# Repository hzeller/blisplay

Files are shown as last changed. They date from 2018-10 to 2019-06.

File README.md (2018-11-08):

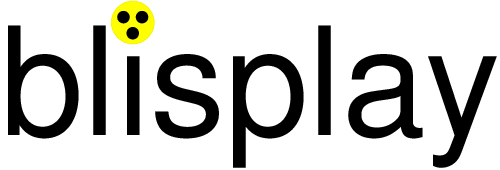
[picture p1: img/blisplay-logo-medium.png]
Blisplay logo


<h1 align="center">an Open Source Hardware tactile display for the blind.</h1>

## Seeing for the blind: make it tactile
Without optical sense there is another way of conveying spatial information
in an accessible way by providing a [tactile experience][tactile-graphic].
Usually, these are 'offline' methods by using swell papers or embossers to
generate a surface representing graphics.

I wanted to make a "display" that can provide such tactile surface directly from
the computer. Of course, it would be a huge effort (and pretty heavy) to build
a surface with tens of thousands of actuators to poke out little dots, so
instead let's just strap a small amount of actuated dots just covering the
fingertip under the finger and actuate them depending on where the finger is
in the image. A display for the blind, let's call it **blisplay**.

#### About this README

I have to apologize to visually impaired readers of this README as it
contains are a couple of pictures in here which make it less accessible.
But these hopefully help your sighted peers to get them started
building the device. To make up for it, there are some explanations that
might sound lengthy and detailed to sighted readers - these are part of the
proverbial thousand words describing the pictures.

#### Direct optical to tactile

There is a simple direct way to do it: mount a camera under the set of tactile
pixels, watching the optical image underneath, directly translating optical
to tactile information; while moving the finger over the surface, the image
underneath will be translated to tactile information, allowing the user to
experience the full image by following the lines on the surface. This is the
first implementation as it is straightforward.

So the first prototype is sitting on a stand-off to be able to watch the
surface underneath.

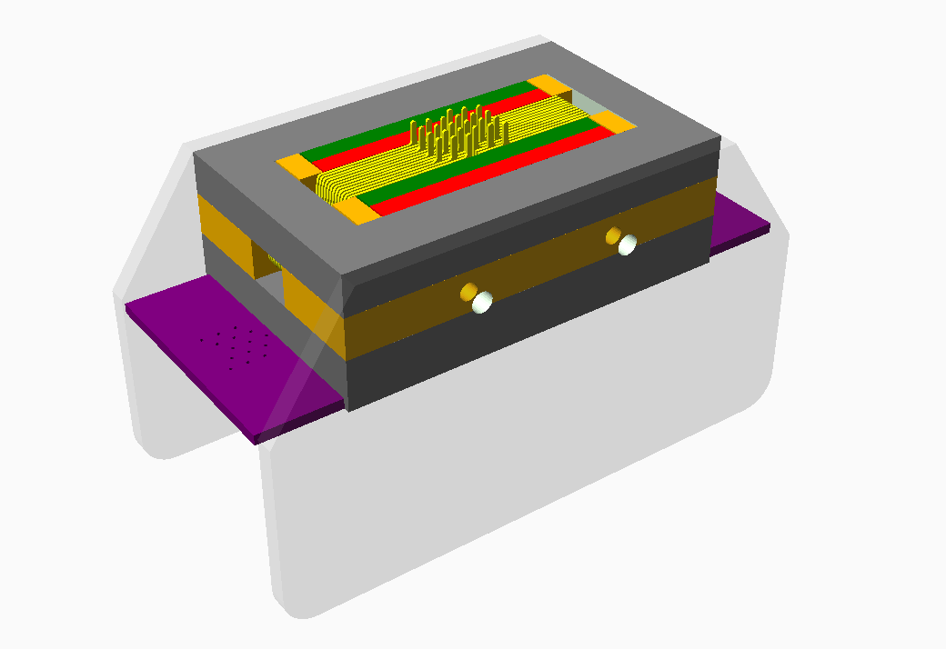
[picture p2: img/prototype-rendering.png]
Rendering of a fully assembled unit
  |
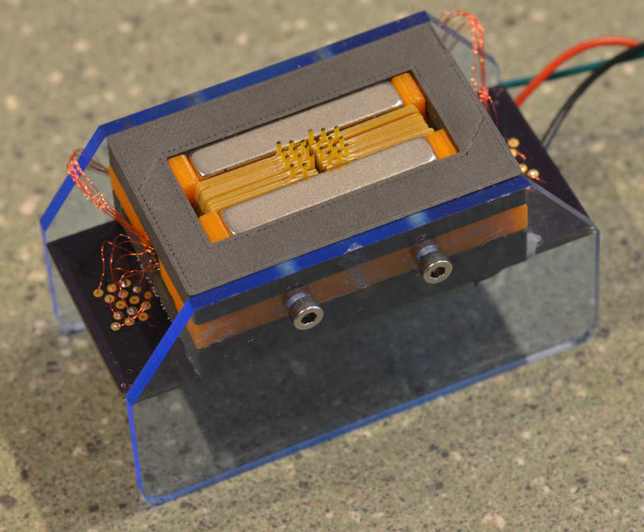
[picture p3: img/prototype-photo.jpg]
Photo of prototype unit
   
-----------------------------------|-------------------------|
Blisplay assembly rendering        | Photo of the actual unit|

#### Display an image from a computer

Another way is to show a picture directly from a computer by having it watch
the position of the finger and present the pixels representing the current
covered area. There are various ways doing it, e.g. with a graphic tablet
encoding the absolute position. Or, these days, it should be easy with the
ubiquitous smart-phones: load an image on the phone and point its camera to
the surface the hand is moving over; with simple image processing, we can
follow the finger relative to the background and send the right tactile
pattern to the device.

### Design goal
The design goal of this project is to make it simple to build
by some technically inclined person for their blind peers.

Right now, I am working on hashing out the most practical way to do so. The
first prototype is already pretty simple, but some more simplification
needs to be done (in particular for the coil wiring, see below).

I would hope for build parties in the future in which hacker-spaces
build devices for their local blind community and improve on the design based
on the feedback.

### Status
The first prototype is assembled and shows desirable functionality and force
of the actuators. The ADNS-3050 chip used as camera is connected but has yet
to be debugged to get some reading of the frame; also the lens-assembly for
getting an image on the sensor has to be worked on.

The current device is a little bit bulky (about 45mmx90mm), but ideas lined-up
for a second prototype will reduce that. Current resolution is about 2mm in a
4x6 grid (8mm x 12mm). This is already pretty close to the spacial resolution of
finger-tips, but future iterations will hopefully improve that more.

### History
What motivated all this ? I have a blind friend for whom I made tactile maps
by gluing thread on paper or transferring graphics using swell-paper
as well as other means to make graphical things accessible.
But in particular I wanted to directly provide images from a computer without
these detours.

In about 2006, I made the very first prototype of this project of a location
aware pixel actuator, [using a modified relay solenoid strapped to a pen of a
graphics tablet](./img/old-prototype-2006.jpg). The single pixels was not very
intuitive though as it requires a lot of scanning by finger. Fast forward do
2018, time to revisit this project and use 3D printing and hobbyist-affordable
PCB making that came up in the meantime to make this much more useful.

## Actuators

There are several ways we could think of actuating raising dots to get the
tactile experience. One of the most important constraints though will be size:
we need to have these pixels reasonably dense and a few of them to be able
to be useful. In the first prototype, these are 4x6 pixels in a 2mm grid
(somewhat diagonal grid as we see later). Also, ideally we can modulate the
force of the pixels to emulate different elevations.

The modulation constraint means that we can't use a bi-stable solenoid but
need to go with a moving coil or moving magnet approach.

The density constraint means that we need to optimize the use of the available
volume for the moving parts and keep supporting structure (magnets, wiring, ...)
out of the way.

### Moving coil
So let's just do the first and simplest thing that comes to mind: use a
conductor in a magnetic field, generating a [Lorentz force].
The conductor is made out of a PCB coil, essentially a square area with a
protruding bit on one side (the tactile dot) and a fulcrum in the
center other side.

#### Stack of flat coils in magnetic field
To visualize (sighted readers also see this in the images): Let's imagine
your left hand facing you with the thumb up.
The hand represents the flat coil with a conductor going across the index
finger towards your wrist, then down, and out again towards the pinkie.

The thumb is extended out and represents the little dot that will poke.
This coil/hand is hinged at the tip of the middle finger.
The magnetic field is going through the flat hand coming from the back of
your hand at the top and at the bottom into your hand pointing towards the back.

With a current through the conductor, the top conductor will move up and so will
the reversed bottom conductor through the reversed magnetic field. This coil
will hinge and move the thumb up and down.

With a stack of these coils, we can have a lot of actuators in a pretty dense
space. A stack of 12 coils are grouped in four stacks of three.
In each triplet, the first coil has the protruding dot the furthest away from
the fulcrum, the next 2mm in (as if the thumb was mounted more towards your
index finger), the next 4mm in.
That way, we can have three independently controlled pixels in that direction.
The coils are made of 0.4mm thick PCB, so the stack can be made 2mm thick with
some wiggle room to spare.
With four of these triplets, we have 4x3 pixels with a 2 mm distance between
adjacent pixels (but slightly diagonal due to the stacking).

In the following demonstration, the current direction is
shown in the traditional plus to minus direction to align with the common
Lorentz right-hand rule.

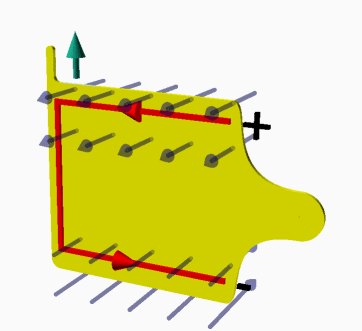
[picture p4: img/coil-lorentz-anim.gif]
Animation of forces in magnetic field
   |
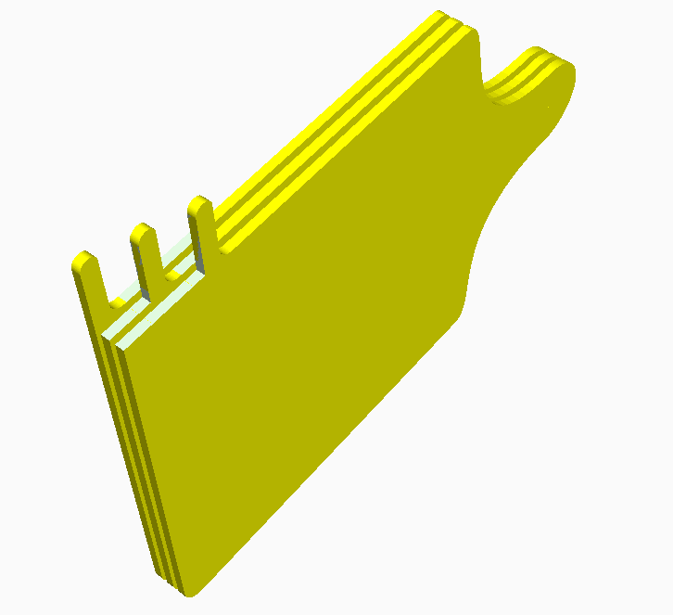
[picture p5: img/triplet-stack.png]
A stack of three coils with offset fingers
 |
-----------------------------------------------|---------------------|
Moving coil in magnetic field. Red arrow: varying current; Blue: static magnetic field; Green: resulting force | A triplet of coils with offset dots, stacked.

If we hinge two stacks right and left with the poky bits meeting at the center
we have a 6x4 pixel arrangement.

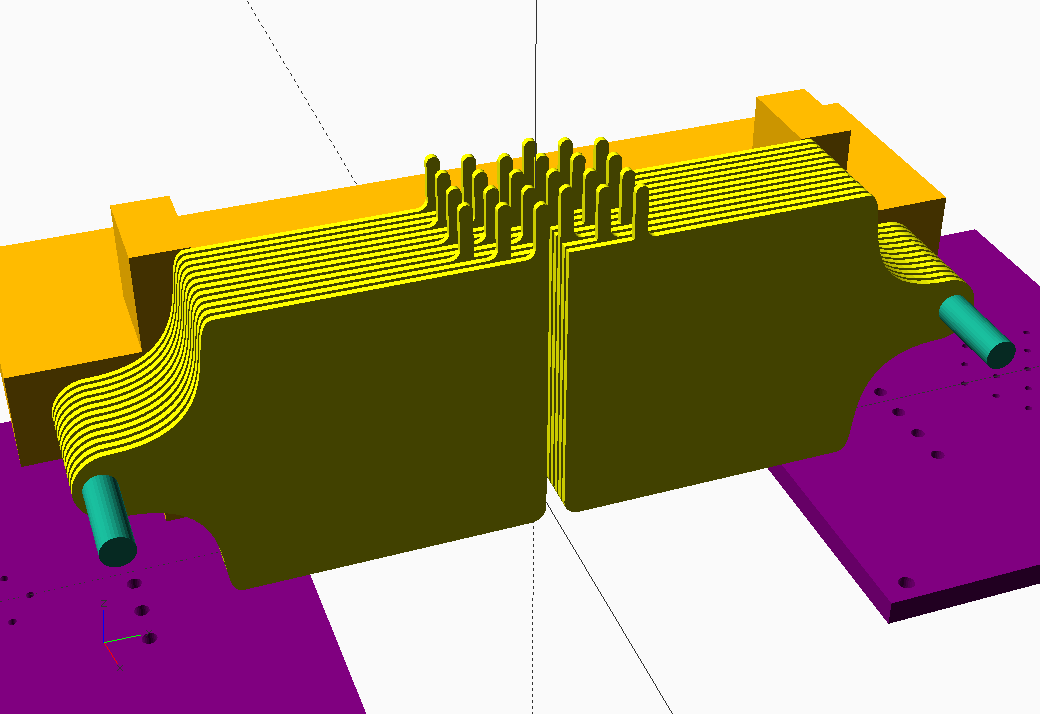
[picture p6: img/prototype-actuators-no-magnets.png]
Rendering showing view of actuators without magnets
 |
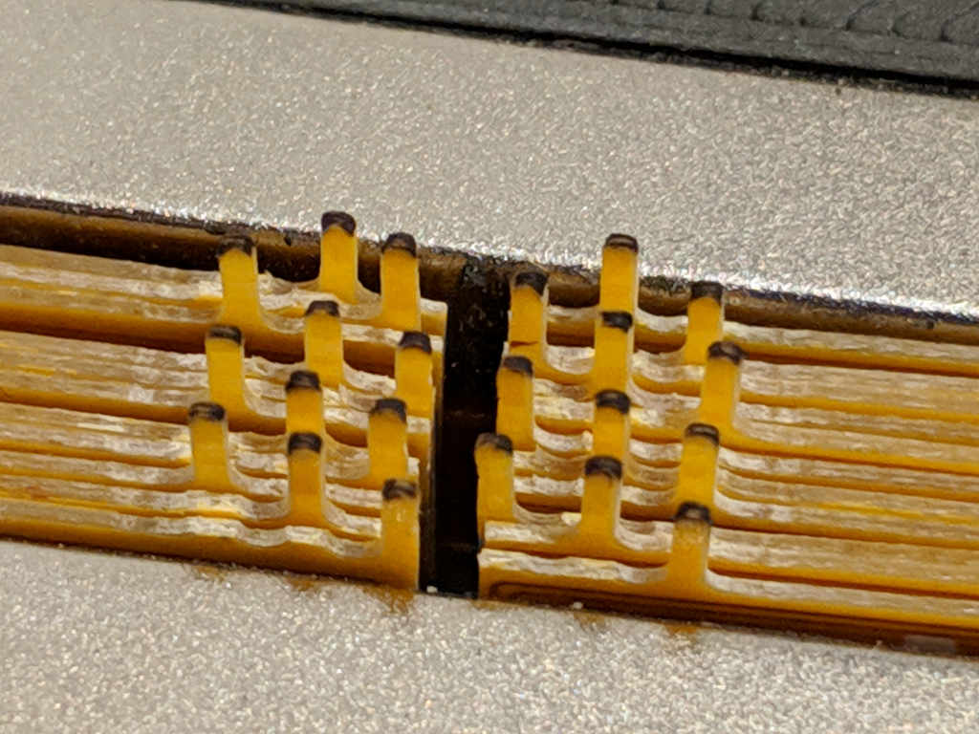
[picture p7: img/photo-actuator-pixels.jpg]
Closeup of pixels in prototype
  
-----------------------------------------------|---------------------|
View of all actuator blade coils. Hinged at opposite ends of the assembly, they allow 6x4 pixels in the center.  | Closeup of pixels in prototype (here, only 22 pixels)

With each blade coil mounted, they can be individually controlled.

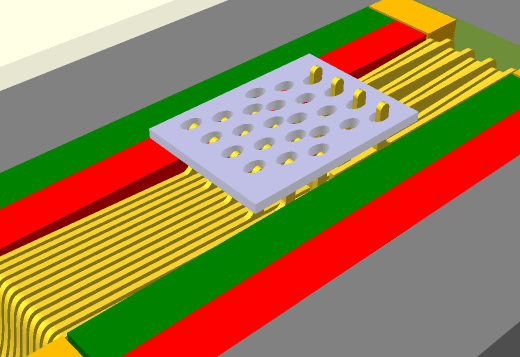
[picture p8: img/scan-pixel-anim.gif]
Animation of pixels scanning and poking through finger-pad


## Driving Circuit

The coils need to be driven in the low hundreds of milliampere; for this simple
transistor drivers are used (maybe in the future half-bridges ?).

The driving circuit for the coils are currently two identical boards with
a shift register and ULN2803 open collector driver chips. The two chained
boards are presenting itself as a 32 bit shift register to the microcontroller
and has two LEDs and allow to connect up to 30 coils. The
latch input is latching on the positive edge, so it can be used as an SPI
client.

The component choice was based on what I had lying around at home, but a
future iteration of this board will be more compact, e.g. by using
NCV7751 chips that contain 12 drivers and an SPI interface in one package
(or maybe TLE94112 with half-bridges).

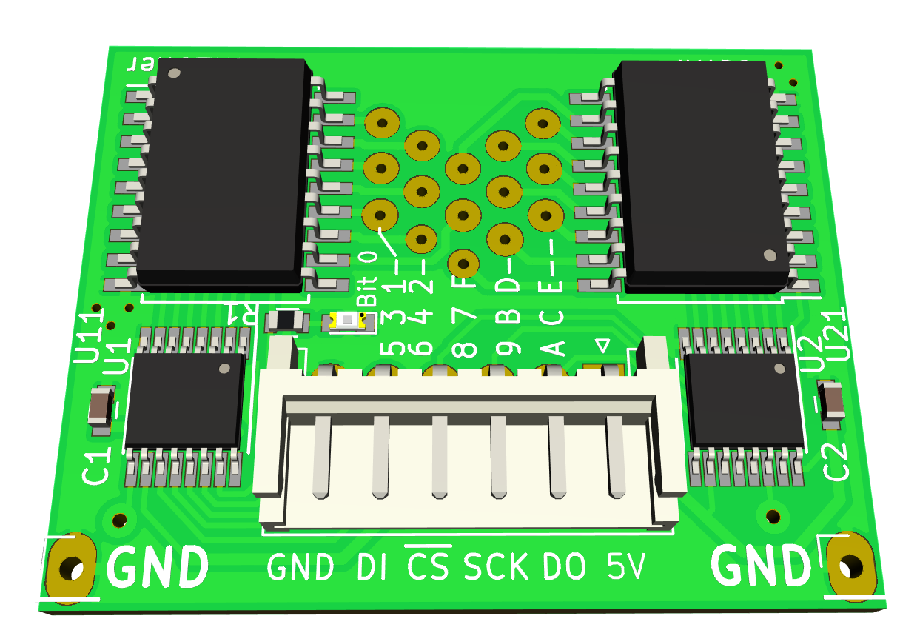
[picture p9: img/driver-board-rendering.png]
Rendering of coil-driver board
 |
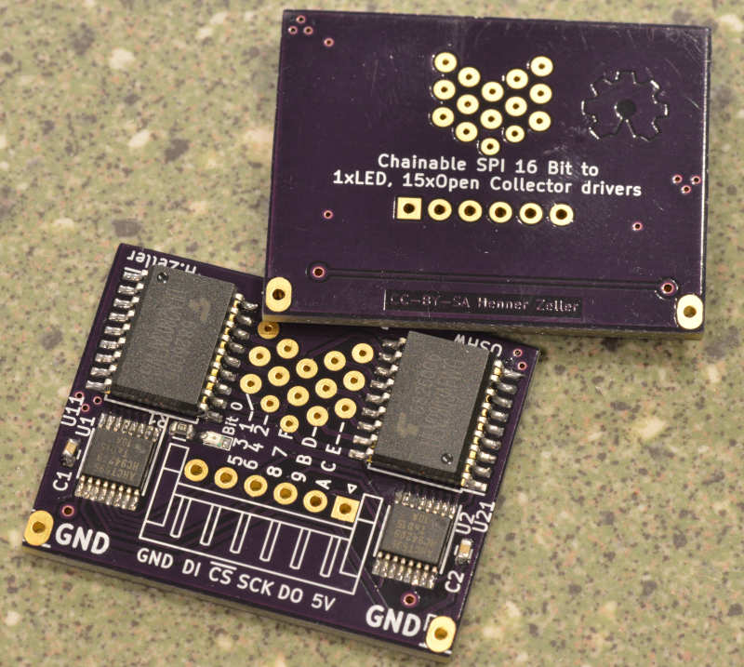
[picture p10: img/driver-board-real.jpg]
Image of soldered coil-driver board
    
--------------------------------------|-----------------------------------|
15 Transistor serial driver board     |  ... for realz                    |

## Controlling Circuit
The controlling circuit right now is a simple ATTINY85 using SPI to
communicate with the driver circuit and the ADNS-3050. Two pins are used as
Chip Select for either the camera or the coil drivers.

This prototype is mounted on a raster board. The camera does not yet
have an optical lens assembly as the readout still needs to be debugged.

A future version will likely use a Microcontroller with more pins (ATTINY44) to
be able to also drive an additional 0.96" OLED display to help visualize while
debugging.

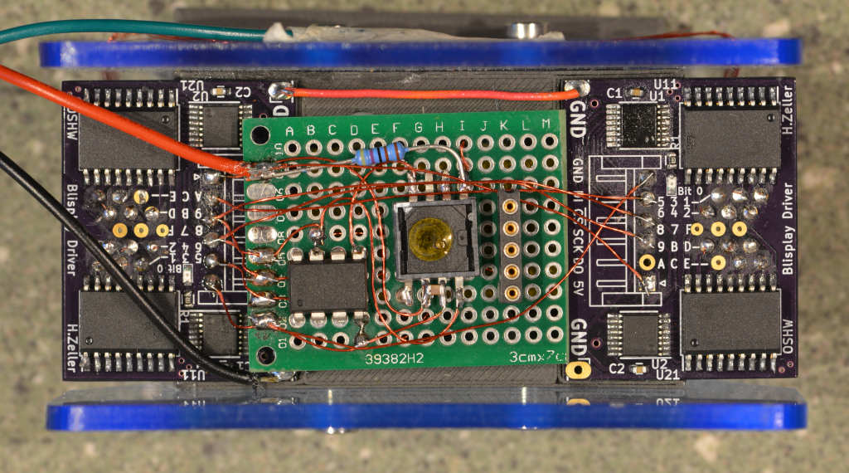
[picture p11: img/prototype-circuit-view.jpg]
Circuit from the bottom of the assembly


# Building

Right now, the prototype design is still somewhat in flux, but you can already
build a prototype. Mail me directly if you have specific questions while doing
so.

### 3D printing and laser cutting

You need to have OpenSCAD installed, then, in the top-level directory, type

```
 make
```

This will generate the following files inside a `fab/` directory:

  * `print_yokes_magnetic_filament.stl` yokes to be printed with magnetic
    filament (I found that magnetic filament is actually not that good. I ended
    up printing them hollow and fill with iron powder. The next prototype will
    just use simple iron parts from the hardware store).
  * `print_yoke_spacers.stl` The spacers, to be printed with regular,
    non-magnetic filament.
  * `lasercut_sidewall.dxf` the side-wall to elevate the assembly to have a
    free view below. These dimensions are super rough right now and will change
    once there is a lens-assembly on the camera.
  * `finger_cradle.stl` is a hollow shape keeping the finger in place over
    the actuators. You might need to adapt parameters to your finger-diameter.
    (currently does not lock into the rest of the assembly, you might need
    some double-sided tape).
  * The `assembly_tool_spacer_holder.stl` is not technically part of the
    blisplay, but a useful tool holding the parts while assembling.
  * In the top-level directory, there is also a PostScript file `coil-shape.ps`
    describing the coil shape, which is converted to a DXF file by the
    Makefile. That is used for the PCBs, but are also imported in the OpenSCAD
    model. Don't worry about these, the generated DXF file is also checked in.
  * For the assembly I am [using magnets][magnet-used] of size
    38.1mm x 6.35mm x 6.35mm.

### Printed circuit boards
Right now, there are two printed circuit boards.

  * The driver boards. These are in the [`driver-pcb/`](./driver-pcb)
    directory. These are likely to change to be more compact. [You can order
    them from OshPark][oshpark-driver] (not affiliated).
  * The coils: In the directory [`coil-pcb/`](./coil-pcb), you find the program
    to generate the coil footprint and a simple KiCAD project putting the
    coil shape and the coil footprint together. Future versions will have a
    slightly different shape (wedge form) and different connecting pads.
    Unfortunately, OshPark does not do 0.4mm thick PCBs, so you have to use
    some other PCB service to make these.
  * There is no microcontroller board yet, right now this is on a raster
    board. Once the optics is figured out, this (and possibly together with
    different driver chips) will be part of the next iteration.

### Wiring up the coils
Wiring up the coils is the most time-consuming currently. The coil-PCBs have
solder points to solder wires to, but just soldering on even a 0.1mm thick
enameled wire already makes them too thick to work well in the assembly.

So in the first iteration, I scratched a tiny groove with a scalpel into the
PCB, then embedded the enameled wire into that grove and soldered it flat
into there. Then insulation covered that with transformer lacquer.
Future experiments certainly will attempt to make this less tedious, e.g.
hot-bar flexible PCB on top of the board instead.

The coil PCB has pokey-bits for all three positions; once the coil is ready to
mount, remove the unused ones with a side-cutter.

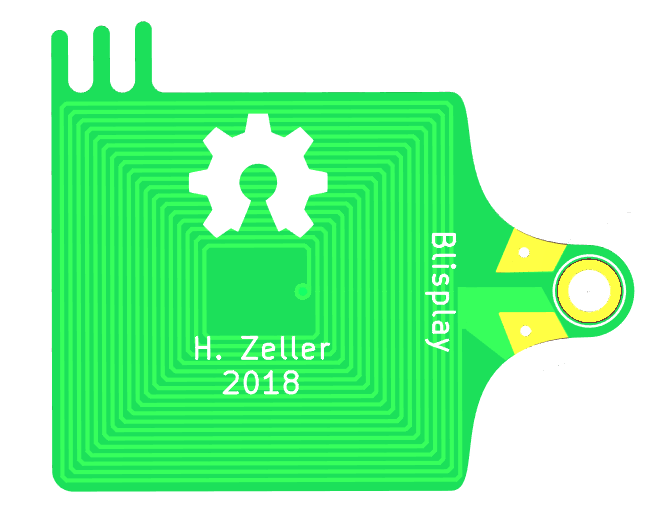
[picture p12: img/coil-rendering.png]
The coil
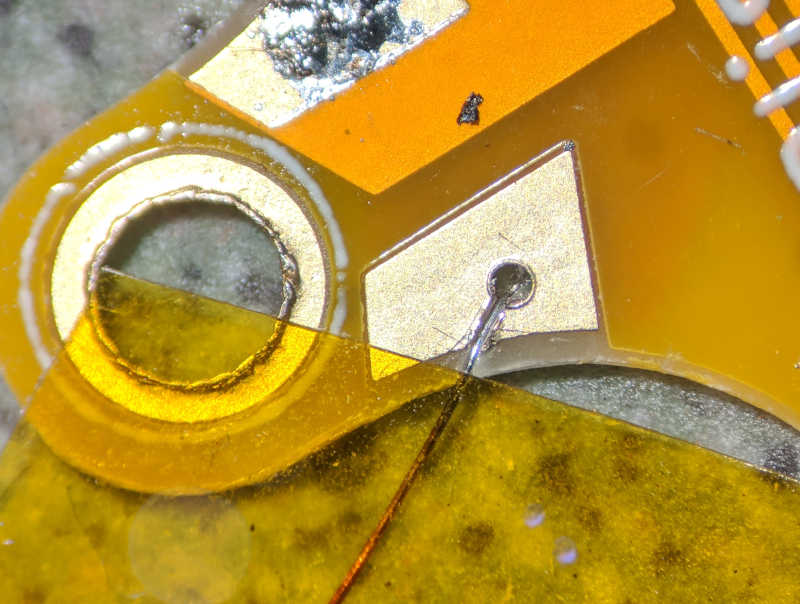
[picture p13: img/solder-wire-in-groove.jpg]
Placing wire in groove
 | 
--------------------------------------|-----------------------------------|
The coil PCB. Unused pokey bits are to be clipped off. Note the different lengths to accommodate the finger curvature. | Placing a wire in groove prepared with scalpel to keep wiring as flat as possible.

The wiring to the driver boards is currently via soldering, but that makes it
a pain to assemble and hard to maintain.
Thus future versions will use flat-flex connectors.

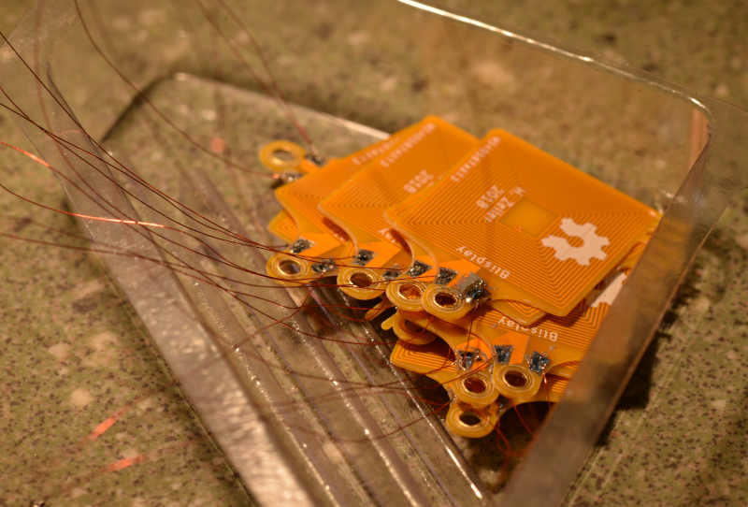
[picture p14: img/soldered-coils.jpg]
finished coils
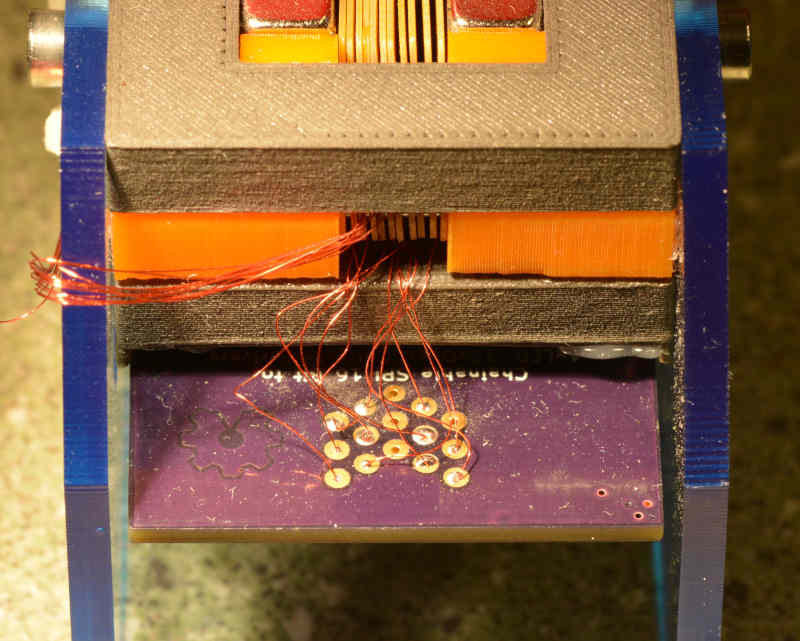
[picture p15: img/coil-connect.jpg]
Wiring coils to driver
      | 
--------------------------------------|-----------------------------------|
Finished coils, ready to mount.       | Wiring of coils to driver board.

### Code
The code is in the [`src/`](./src) sub-directory. Build with the makefile
there, then flash using an Atmel programmer via avrdude (`make flash`).

# License
Any PCBs and 3D printed parts are Open Source Hardware licensed
with `CC-BY-SA` license. Any code is licensed with the GPL v3.

[logo]: ./img/blisplay-logo-medium.png
[img-render-oblique]: ./img/prototype-rendering.png
[img-photo-oblique]: ./img/prototype-photo.jpg
[img-render-no-magnets]: ./img/prototype-actuators-no-magnets.png
[img-photo-pixels]: ./img/photo-actuator-pixels.jpg
[img-anim-lorentz]: ./img/coil-lorentz-anim.gif
[img-triplet-coil]: ./img/triplet-stack.png
[img-anim-pixel-scan]: ./img/scan-pixel-anim.gif
[img-circuit]: ./img/prototype-circuit-view.jpg
[magnet-used]: https://www.kjmagnetics.com/proddetail.asp?prod=BX844
[tactile-graphic]: https://en.wikipedia.org/wiki/Tactile_graphic
[Lorentz force]: https://en.wikipedia.org/wiki/Lorentz_force
[oshpark-driver]: https://oshpark.com/shared_projects/nWsVpTrj
[coil-groove]: ./img/solder-wire-in-groove.jpg
[coil-render]: ./img/coil-rendering.png
[coil-finished]: ./img/soldered-coils.jpg
[coil-attached]: ./img/coil-connect.jpg

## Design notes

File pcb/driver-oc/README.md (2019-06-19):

An open collector driver.

Distance Flat flex: 21mm

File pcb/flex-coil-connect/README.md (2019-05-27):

Flex connector
==============

Connects the driver board with the coil-blades.

Currently first experimental board. Shape is generated with
PostScript, then the converted DXF is imported as Edge.Cuts.

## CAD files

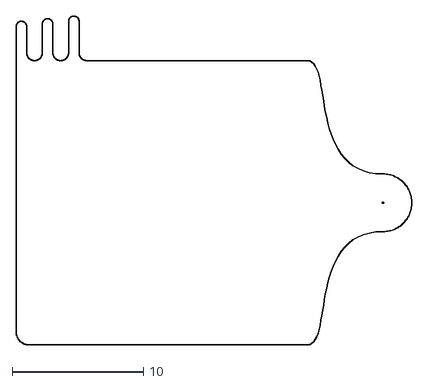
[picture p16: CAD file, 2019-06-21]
pcb/coil/coil-edge-cuts.dxf
30.2 x 25.1

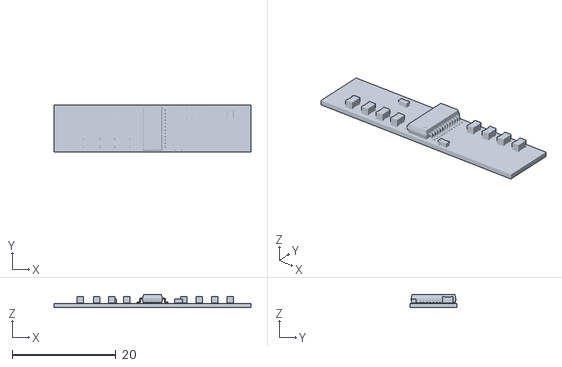
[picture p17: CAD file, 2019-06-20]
pcb/driver-oc/blisplay-driver-oc.stl
38.0 x 9.00 x 2.50

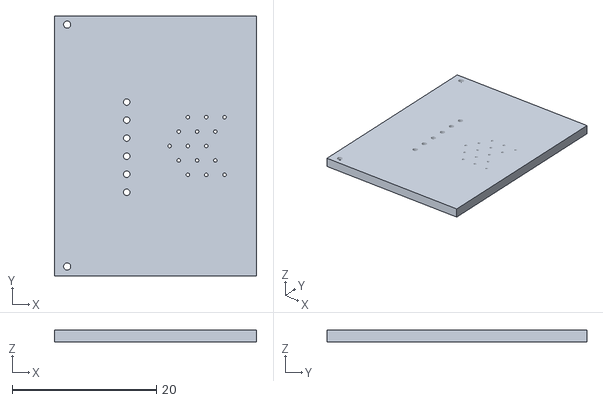
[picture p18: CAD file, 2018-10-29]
pcb/driver-v0/blisplay-driver.stl
28.0 x 36.0 x 1.60

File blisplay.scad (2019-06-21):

$fn=120;
e=0.01;

acrylic_t = 3;   // Acrylic thickness for laser-cut parts

// The "display" dots.
dots_x=4;
dots_y=6;
dot_dist=2;
dot_dia=1;

// The magnets.
mag_len=1.5*25.4;   // Length of the whole magnet
mag_w=25.4/4;       // width of the poles we look at.
mag_thick=25.4/4;   // Poles are on opposite ends of the thickness

// Driver PCB.
driver_board_width=38;
driver_board_height=9;
driver_board_thick=0.8;
driver_flex_distance=21;

space_between_magnets=driver_board_height;
coil_height=2*mag_w + space_between_magnets;
coil_thick=0.4;

yoke_wall=25.4/8;      // thickness of yoke material.
yoke_transparency = 0.5;

center_w=dots_x * dot_dist;

yoke_width = center_w + 2*mag_thick+2*yoke_wall;

poke_len=2;
poke_off_angle=-3;
poke_on_angle=0;

flex_width=2;
stack_layer_count = (dots_y * dots_x) / 2;  // half on each side

// To be shared with the postscript.
fulcrum_dia=2;
fulcrum_ring=1;
fulcrum_distance=28;

optical_clearance = 30;   // Clearance at the bottom for the optical system

echo("Coil PCB size: ", coil_height + poke_len, "x",
     fulcrum_distance+fulcrum_dia+fulcrum_ring);

module finger_cradle(elevate=2.5, finger_diameter=20, finger_hug_height=6) {
     fh=finger_hug_height;
     fr=finger_diameter / 2;
     actuator_space=1.2;   // Space above actuators, e.g. for dampening felt.
     translate([0,0,elevate]) difference() {
	  hull() {  // Outer space.
	       intersection() {
		    translate([0, 0, fr-0.5]) scale([1, 1.6, 1]) sphere(r=fr+0.5);
		    translate([0,0,fh/2]) cube([20, 32, fh], center=true);
	       }
	       translate([0,-8,fh/2]) cube([20, 16, fh], center=true);
	       translate([0,0,-elevate+0.5]) cube([yoke_width, 32, 1], center=true);
	  }
	  hull() {  // Space to keep felt dampener
	       translate([0, 0, -elevate+actuator_space]) cube([4*2+2, 35+2*e, e], center=true);
	       translate([0, 0, -elevate-e]) cube([4*2+6, 35+2*e, e], center=true);
	  }
	  // Punch the space for the actuator pins to come through.
	  punch_height=fh+elevate;
	  punch_corner_r=2;
	  punch_w = (dots_x*dot_dist+1)/2 - punch_corner_r;
	  punch_h = (dots_y*dot_dist+1)/2 - punch_corner_r;
	  // Make a rounded corner hole.
	  translate([0, 0, -punch_height/2]) hull() {
	       translate([punch_w, punch_h, 0]) cylinder(r=punch_corner_r, h=punch_height);
	       translate([-punch_w, punch_h, 0]) cylinder(r=punch_corner_r, h=punch_height);
	       translate([-punch_w, -punch_h, 0]) cylinder(r=punch_corner_r, h=punch_height);
	       translate([punch_w, -punch_h, 0]) cylinder(r=punch_corner_r, h=punch_height);
	  }
	  translate([0, 0, fr-0.5]) scale([1, 1.2, 1]) sphere(r=fr);
	  //translate([0, 0, fr+0.5]) rotate([90, 0, 0]) cylinder(r=fr, h=20);
     }
}

module magnet() {
     color("red") translate([-mag_thick/2,-mag_len/2,0]) cube([mag_thick/2, mag_len, mag_w]);
     color("green") translate([0,-mag_len/2,0]) cube([mag_thick/2, mag_len, mag_w]);
}


module yoke(with_magnet=false) {
     translate([-mag_thick, 0, -coil_height/2]) {
	  color([0.5, 0.5, 0.5, yoke_transparency])
	       translate([-yoke_wall, -mag_len/2, 0])
	       cube([yoke_wall, mag_len, coil_height]);
	  if (with_magnet) {
	       translate([mag_thick/2, 0, 0]) magnet();
	       translate([mag_thick/2, 0, coil_height]) rotate([0,180,0]) magnet();
	  }
     }
     translate([-mag_thick, 0, 0]) driver_board();
}

module coil(poke_pos=0, is_poke) {
     //echo(poke_pos, " -> ", is_poke);
     poke_width=0.8;
     translate([0, fulcrum_distance-0.5, coil_height/2])
     rotate([is_poke ? -poke_on_angle : -poke_off_angle, 0, 0]) translate([0, -fulcrum_distance+0.5, -coil_height/2])
	  color("#00ef00") render() difference() {
	       translate([0, (dot_dist-poke_width)/2, 0]) rotate([90, 0, 90])
	       linear_extrude(height=coil_thick, center=true, convexity = 10)
	       import (file = "pcb/coil/coil-edge-cuts.dxf");
	  // Remove the fingers that we're not interested in.
	  for (i = [0:3]) {
	       if (i != poke_pos) {
		    translate([-1, (dot_dist-poke_width)/2 + i*dot_dist-0.5, coil_height])
			 cube([2, dot_dist+0.5, 5]);
	       }
	  }
     }
}

module coil_triplet(x_pos, poke_array) {
     translate([-dot_dist/3, 0, 0])
	  coil(0, is_poke=poke_array[2*dots_x + x_pos]);
     angle = 0;
     translate([0, fulcrum_distance, coil_height/2]) rotate([angle,0,0])
	  translate([0, -fulcrum_distance, -coil_height/2])
	  coil(1, is_poke=poke_array[1*dots_x + x_pos]);
     translate([dot_dist/3, 0, 0])
	  coil(2, is_poke=poke_array[0*dots_x + x_pos]);
}

module coil_stack(poke_array) {
     //echo("poke", poke_array);
     offset = (dots_x-1) * dot_dist / 2.0;
     for (i = [0:1:dots_x-e]) {
	  translate([i * dot_dist - offset, 0, 0])
	       coil_triplet(i, poke_array);
     }
}

module actuators(poke_array) {
     rotate([0,0,180]) coil_stack(poke_array=poke_array);

     // The back is rotated and turned, so easy if we just map flipped array
     reflect_array = [for (i = [0:24]) poke_array[23-i]];
     coil_stack(poke_array=reflect_array);
}

module magnet_assembly() {
     translate([-center_w/2, 0, coil_height/2]) yoke(with_magnet=true);
     translate([center_w/2, 0, coil_height/2]) rotate([180,0,180]) yoke(with_magnet=true);
}

module fulcrum_axles() {
     // Fulcrum axles.
     fulcrum_len=dots_x * dot_dist + 2*mag_thick;
     color("silver") translate([0, fulcrum_distance, coil_height/2])
	  rotate([0,90,0]) translate([0,0,-fulcrum_len/2]) cylinder(r=fulcrum_dia/2, h=fulcrum_len);
     color("silver") translate([0, -fulcrum_distance, coil_height/2])
	  rotate([0,90,0]) translate([0,0,-fulcrum_len/2]) cylinder(r=fulcrum_dia/2, h=fulcrum_len);
}

module driver_board(realistic=true) {
     color("lightgreen") {
	  rotate([0, 90, 0]) rotate([0, 0, 90]) translate([-119, 54.5, 0]) import(file = "pcb/driver-oc/blisplay-driver-oc.stl");
     }
}

module yoke_spacer_screw() {
     round_edge_radius=fulcrum_dia/2 + 2;
     color("#FFBB00") translate([center_w/2, 0, 0]) {
	  // Distance holders
	  translate([-center_w, -fulcrum_distance, coil_height/2-round_edge_radius]) rotate([0, 90, 0]) difference() {
	       cylinder(r=round_edge_radius, h=center_w);
	       translate([0, 0, -e]) cylinder(r=3.2/2, h=center_w+2*e);
	  }
	  translate([-center_w, fulcrum_distance, -coil_height/2+round_edge_radius]) rotate([0, 90, 0]) difference() {
	       cylinder(r=round_edge_radius, h=center_w);
	       translate([0, 0, -e]) cylinder(r=3.2/2, h=center_w+2*e);
	  }
     }
}

// TODO: this is a lot of empty space in the yoke-spacer, that we can fill
// with electronics later.
module yoke_spacer() {
     round_edge_radius=fulcrum_dia/2 + 2;
     yoke_outer_wall = (yoke_width - center_w)/2;
     color("#FFBB00") translate([center_w/2,0,0]) {
	  difference() {
	       union() {
		    // center piece, probably later more hollow for electronics
		    translate([mag_thick/2,0,0]) cube([mag_thick, mag_len, space_between_magnets], center=true);

		    hull() {
			 translate([0, mag_len/2, -coil_height/2]) cube([mag_thick+yoke_wall, e, coil_height]);
			 translate([0, fulcrum_distance, coil_height/2-round_edge_radius]) rotate([0, 90, 0]) cylinder(r=round_edge_radius, h=mag_thick+yoke_wall);
			 translate([0, fulcrum_distance, -coil_height/2+round_edge_radius]) rotate([0, 90, 0]) cylinder(r=round_edge_radius, h=mag_thick+yoke_wall);
		    }

		    hull() {
			 translate([0, -mag_len/2, -coil_height/2]) cube([mag_thick+yoke_wall, e, coil_height]);
			 translate([0, -fulcrum_distance, coil_height/2-round_edge_radius]) rotate([0, 90, 0]) cylinder(r=round_edge_radius, h=mag_thick+yoke_wall);
			 translate([0, -fulcrum_distance, -coil_height/2+round_edge_radius]) rotate([0, 90, 0]) cylinder(r=round_edge_radius, h=mag_thick+yoke_wall);
		    }
	       }

	       // Holes for the fulcrum. Not entirely punched through to the end
	       translate([-e, fulcrum_distance, 0]) rotate([0,90,0]) cylinder(r=fulcrum_dia/2+0.2, h=yoke_outer_wall-1);
	       translate([-e, -fulcrum_distance, 0]) rotate([0,90,0]) cylinder(r=fulcrum_dia/2+0.2, h=yoke_outer_wall-1);

	       // Screw for the distance holders
	       translate([mag_thick+yoke_wall, -fulcrum_distance, coil_height/2-round_edge_radius]) rotate([0, -90, 0]) mount_screw(h=yoke_width);

	       // Crude cut-out to have a smooth screw holder
	       translate([mag_thick+yoke_wall-2+e, -fulcrum_distance-3, coil_height/2-round_edge_radius]) cube([4, 6, 6], center=true);
	       translate([mag_thick+yoke_wall-2+e, -fulcrum_distance, coil_height/2-round_edge_radius+3]) cube([4, 6, 6], center=true);

	       translate([mag_thick+yoke_wall-2+e, +fulcrum_distance+3, -coil_height/2+round_edge_radius]) cube([4, 6, 6], center=true);
	       translate([mag_thick+yoke_wall-2+e, fulcrum_distance, -coil_height/2+round_edge_radius-3]) cube([4, 6, 6], center=true);

	       translate([mag_thick+yoke_wall, +fulcrum_distance, -coil_height/2+round_edge_radius]) rotate([0, -90, 0]) mount_screw(h=yoke_width);
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

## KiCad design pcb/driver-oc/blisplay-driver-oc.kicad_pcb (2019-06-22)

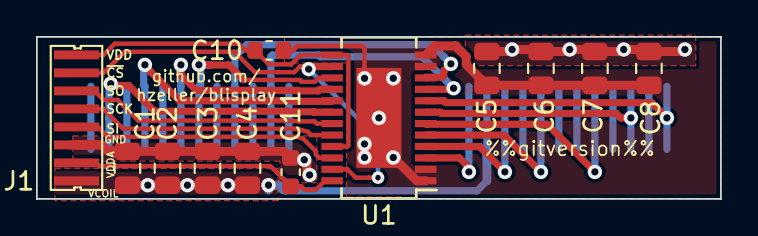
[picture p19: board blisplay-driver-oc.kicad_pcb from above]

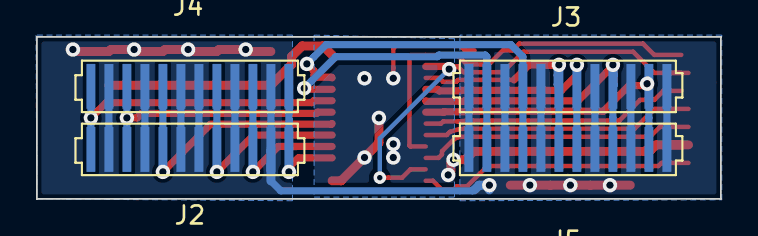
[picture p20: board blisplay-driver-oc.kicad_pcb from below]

Board: 2 copper layers, 38.0 x 9.0 mm, 16 parts (4 on the bottom side), 20 nets.

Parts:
C1, C2, C3, C4, C5, C6, C7, C8: 10μ; C_0805_2012Metric
C10, C11: 100n; C_0603_1608Metric
J1: Conn_01x08; driver-connect
J2, J3, J4, J5: Flex; flex-12
U1: NCV7751; SSOP-24EP_3.9x8.7mm_P0.635mm

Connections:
/Coil_1: J2.1, J4.1, U1.3
/Coil_2: J2.3, J4.3, U1.4
/Coil_3: J2.5, J4.5, U1.5
/Coil_4: J2.8, J4.8, U1.6
/Coil_5: J2.10, J4.10, U1.7
/Coil_6: J2.12, J4.12, U1.8
/Coil_7: J3.2, J5.2, U1.9
/Coil_8: J3.4, J5.4, U1.10
/Coil_9: J3.6, J5.6, U1.15
/Coil_10: J3.7, J5.7, U1.16
/Coil_11: J3.9, J5.9, U1.17
/Coil_12: J3.11, J5.11, U1.18
/SCK: J1.4, U1.20
/SI: J1.5, U1.22
/SO: J1.3, U1.19
/VCOIL: C1.1, C2.1, C3.1, C4.1, C5.1, C6.1, C7.1, C8.1, J1.8, J2.2, J2.4, J2.6, J2.7, J2.9, J2.11, J3.1, J3.3, J3.5, J3.8, J3.10, J3.12, J4.2, J4.4, J4.6, J4.7, J4.9, J4.11, J5.1, J5.3, J5.5, J5.8, J5.10, J5.12
/~CS: J1.2, U1.14, U1.23
GND: C1.2, C2.2, C3.2, C4.2, C5.2, C6.2, C7.2, C8.2, C10.2, C11.2, J1.6, U1.0, U1.1, U1.2, U1.11, U1.12
VDD: C10.1, J1.1, U1.13, U1.21
VDDA: C11.1, J1.7, U1.24

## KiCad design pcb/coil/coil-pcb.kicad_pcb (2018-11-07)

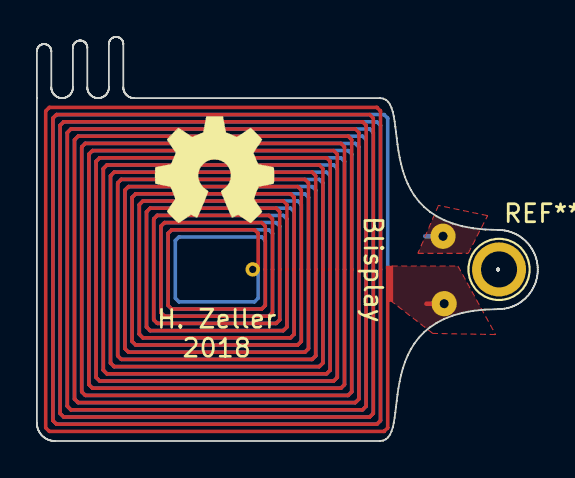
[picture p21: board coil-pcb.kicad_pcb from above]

Board: 2 copper layers, 27.8 x 22.5 mm, 3 parts (0 on the bottom side), 2 nets.

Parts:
J1, J2: Conn_01x01; Pin_d0.7mm_L6.5mm_W1.8mm_FlatFork
L1: INDUCTOR; coil

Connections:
A: J1.1, L1.1
B: J2.1, L1.2

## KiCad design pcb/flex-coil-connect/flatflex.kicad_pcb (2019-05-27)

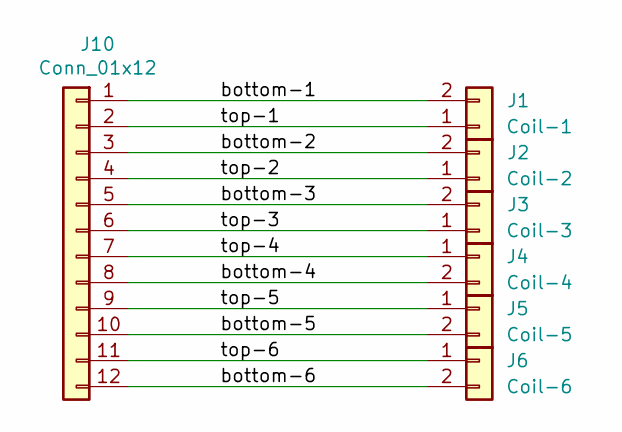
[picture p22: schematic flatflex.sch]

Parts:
J1: Coil-1; flex-coil-connect
J2: Coil-2; flex-coil-connect
J3: Coil-3; flex-coil-connect
J4: Coil-4; flex-coil-connect
J5: Coil-5; flex-coil-connect
J6: Coil-6; flex-coil-connect
J10: Conn_01x12; flex-12

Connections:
/bottom-1: J1.2, J10.1
/bottom-2: J2.2, J10.3
/bottom-3: J3.2, J10.5
/bottom-4: J4.2, J10.8
/bottom-5: J5.2, J10.10
/bottom-6: J6.2, J10.12
/top-1: J1.1, J10.2
/top-2: J2.1, J10.4
/top-3: J3.1, J10.6
/top-4: J4.1, J10.7
/top-5: J5.1, J10.9
/top-6: J6.1, J10.11

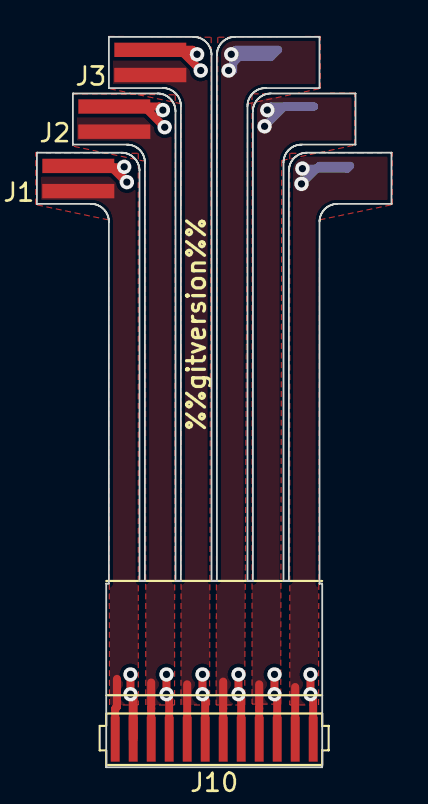
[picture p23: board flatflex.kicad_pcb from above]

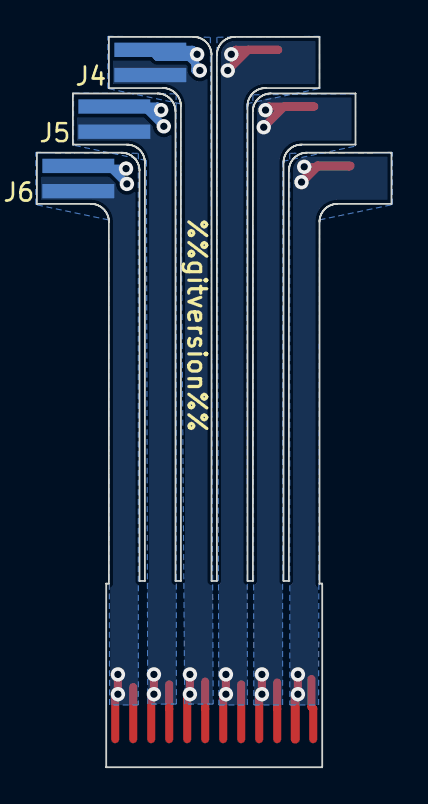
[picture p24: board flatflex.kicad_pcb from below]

Board: 2 copper layers, 19.7 x 40.6 mm, 7 parts (3 on the bottom side), 12 nets.

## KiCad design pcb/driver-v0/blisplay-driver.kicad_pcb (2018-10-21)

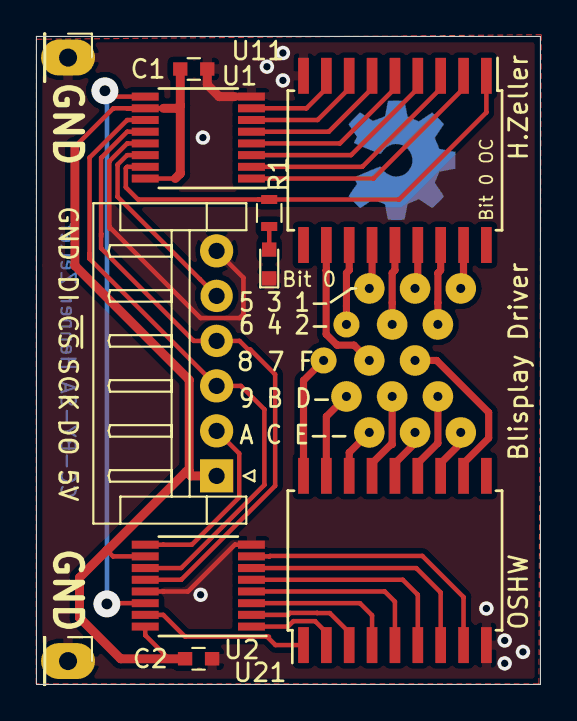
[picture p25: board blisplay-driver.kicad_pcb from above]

Board: 2 copper layers, 28.0 x 36.0 mm, 16 parts (0 on the bottom side), 39 nets.

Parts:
C1, C2: C; C_0603
D1: LED; LED_0603
J1: Conn_01x06; JST_EH_S06B-EH_06x2.50mm_Angled
J2, J3, J4, J5, J6: Conn_01x03; Pin_Header_Straight_1x03_Pitch2.54mm
J7, J8: Conn_01x01; Pin_Header_Straight_1x01_Pitch2.54mm
R1: 1k; R_0603
U1, U2: 74HC595; TSSOP-16_4.4x5mm_Pitch0.65mm
U11, U21: ULN2803A; SOIC-18W_7.5x11.6mm_Pitch1.27mm

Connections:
+5V: C1.1, C2.1, J1.1, U1.10, U1.16, U2.10, U2.16
/Bit0: R1.1, U1.15, U11.1
/CS: J1.4, U1.12, U2.12
/MISO: J1.2, U2.9
/MOSI: J1.5, U1.14
/SCK: J1.3, U1.11, U2.11
/carry: U1.9, U2.14
GND: C1.2, C2.2, D1.1, J1.6, J7.1, J8.1, U1.8, U1.13, U2.8, U2.13, U11.9, U21.9
unnamed: D1.2, R1.2
unnamed: J2.1, U21.16
unnamed: J2.2, U21.14
unnamed: J2.3, U21.12
unnamed: J3.1, U21.17
unnamed: J3.2, U21.15
unnamed: J3.3, U21.13
unnamed: J4.1, U21.18
unnamed: J4.2, U11.11
unnamed: J4.3, U21.11
unnamed: J5.1, U11.12
unnamed: J5.2, U11.14
unnamed: J5.3, U11.16
unnamed: J6.1, U11.13
unnamed: J6.2, U11.15
unnamed: J6.3, U11.17
unnamed: U1.1, U11.2
unnamed: U1.2, U11.3
unnamed: U1.3, U11.4
unnamed: U1.4, U11.5
unnamed: U1.5, U11.6
unnamed: U1.6, U11.7
unnamed: U1.7, U11.8
unnamed: U2.1, U21.2
unnamed: U2.2, U21.3
unnamed: U2.3, U21.4
unnamed: U2.4, U21.5
unnamed: U2.5, U21.6
unnamed: U2.6, U21.7
unnamed: U2.7, U21.8
unnamed: U2.15, U21.1

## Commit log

2014-02-19 Reactivate Blisplay project. Moving magnet will allow for faster reaction time and less 'clicking'; but also less force than solenoid.
    [blisplay.scad]
2018-08-25 More compact coil packing by putting them all in the same homogenized magnetic field. Simplest of all actuators: just straight conductor in perpendicular field.
    [blisplay.scad]
2018-08-25 Make coil shape more pleasing by using bezier curves (generate shape in PostScript, convert to DXF, then use in OpenSCAD).
    [blisplay.scad]
2018-10-07 Coil PCB to be used inside Blisplay.
    o Programmatically generate KiCAD module for a two layer board
    coil.
    o Use DXF generated from PostScript as EdgeCuts outline for
    nice smooth shape (always making sure to have fillets in
    inner corners to be able to be manufuactured. DFM).
    [coil-pcb.kicad_pcb, coil-pcb.sch]
2018-10-21 First version of coil driver board.
    [blisplay-driver.kicad_pcb, blisplay-driver.sch]
2018-10-29 Make cut-out in lower yoke for driver PCBs.
    [blisplay-driver.stl, blisplay.scad]
2018-10-29 Parametrize yoke_spacer to include the dynamic width (which depends on the PCB).
    [blisplay.scad]
2018-10-29 Add mounting holes to pull spacers solid in place.
    [blisplay.scad]
2018-10-30 Add tool helpful for assembly. Provide a 'cover' for yoke.
    The yoke-cover is for the case it is printed hollow and filled with
    iron powder; then we need a lid to glue on.
    [blisplay.scad]
2018-10-31 Add laser-cuttable side-walls.
    [blisplay.scad]
2018-10-31 Add coil shape DXF, so that it does not need to be re-created on checkout.
    [coil-shape.dxf]
2018-10-31 Automatically generate STLs and DXF via Makefile.
    [blisplay.scad]
2018-10-31 some better names for printable modules.
    [blisplay.scad]
2018-11-04 Simulate actuators given an array of poxels.
    [blisplay.scad]
2018-11-06 Have a visualization angle of actuators for 'on' and 'off'
    [blisplay.scad]
2018-11-06 Map coils to current wiring.
2018-11-07 Add a finger-holder, replacing the flimsy finger-pad.
    [blisplay.scad]
2018-11-07 Rename 'finger_holder' to better name 'finger_cradle'
    [blisplay.scad]
2018-11-07 Have slightly shorter Pokey-Pins towards the center, matching finger curvature.
    [coil-pcb.kicad_pcb, coil-shape.dxf]
2018-11-07 Cleanup: move driver-PCB 3D shape used for illustration in scad file into driver-pcb/
    [blisplay-driver.stl, blisplay.scad]
2018-11-08 More coil-wiring pictures; improved picture captions.
2018-11-11 Smaller version, using steel from hardware store for yoke.
    [blisplay.scad]
2018-11-15 Next step wiring: flat flex.
2018-11-17 Add some flat-flex connection rendering.
    [blisplay.scad]
2019-05-27 Refine flatflex-outline. Make first experimental board out of it.
    [flatflex.kicad_pcb, flatflex.sch]
2019-05-27 Reorganize PCBs to be all in one sub-directory.
    Rename blisplay-driver to driver-v0 to not conflict with new
    drivers.
    [blisplay-driver.kicad_pcb, blisplay-driver.sch, blisplay-driver.stl, blisplay.scad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]
2019-05-27 Move coil-edge-cuts dxf in the coil/pcb directory.
    [coil-edge-cuts.dxf]
2019-05-27 Make possible to read driver board with new KiCAD
    Not much effort to convert, as this is going to go anyway.
    [blisplay-driver.sch]
2019-06-19 Adapt wiring to two-sided powering.
    [blisplay.scad]
2019-06-19 Start driver-board to sit between the magnets.
    [blisplay-driver-oc.kicad_pcb, blisplay-driver-oc.sch]
2019-06-19 Add simple connector to driver board.
    This is not mirror symmetric which would be nicer for hassle-free
    wiring. Maybe there should be two variants.
    [blisplay-driver-oc.kicad_pcb, blisplay-driver-oc.sch]
2019-06-20 Make assembly a little higher to accomodate new driver board size.
    [blisplay-driver-oc.stl, blisplay.scad, coil-edge-cuts.dxf]
2019-06-21 Initial, fully routed version of open collector driver.
    [blisplay-driver-oc.kicad_pcb, blisplay-driver-oc.sch]
2019-06-21 Larger coils to accomodate driver PCB. Also: Remove obsolete modules.
    [blisplay.scad, coil-edge-cuts.dxf]
2019-06-22 Label coil circuits. Pull EN to VDD.
    [blisplay-driver-oc.kicad_pcb, blisplay-driver-oc.sch]

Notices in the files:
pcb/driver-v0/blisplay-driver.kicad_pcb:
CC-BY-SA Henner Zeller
